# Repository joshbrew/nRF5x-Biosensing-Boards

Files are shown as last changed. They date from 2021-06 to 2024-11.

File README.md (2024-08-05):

# nRF52/53 Biosensing Boards

This contains our working prototypes for using nRF52 and nRF53 microcontrollers (ARM + BLE5) with low cost sensors. [Doc](https://docs.google.com/document/d/1gOrWiBDynYziCYDMF4r1Rw85PXo9JbuBrYJEEkW2U-c/edit?usp=sharing). 

License: AGPL v3.0 copyleft (public domain). You may do whatever you want with our designs, but you are obligated to share your modifications and advancements publicly. This is in hopes of facilitating a better community around useful wearable medical hardware designs.

The current prototypes here are working breakout boards. They are pin compatible with several different modules while it's easy to spin up new designs with similar products by Fanstel.

Features Zephyr RTOS test firmware, which is hardware-agnostic. 

### Designs included

- BT40/BT840, pin compatible with any Fanstel BT-series but mind the pinouts as not all will work without modification, but most should.
- BC840M
- BC40M
- BT832A (do not use, this was our first attempt)

### Firmware included

- nRF5340
- nRF52840
- nRF52810 (for the BT832A prototype)

### Sensor Support 
- ADS131M08 (8 channel sigma delta converter), there is one on-board 
- MPU6050 accelerometer
- QMC5883L magnetometer (for 9-axis movement when combined with MPU6050)
- MAX30102 pulse oximeter, 
- BMP/BME280 environmental sensor, 
- Additional 8 channel ADS131M08 for up to 16 raw data channels, each individually configurable. 
- MAX98357A Audio output amplifier
- B079Q8G7N1 PDM MEMS microphone

### [Driver Docs](https://docs.google.com/document/d/1eThhvpdm9zZMaKTB0dwuHXi1aBz_5ESBecHRZPxs0kE/edit?usp=sharing)

You can fairly easily add more sensor modules, which are all plug-and-play so the board can run with any combination of sensors. We'll clean this up more as we go for easier customization and feature inclusions. The BT840/BT40, BC840M, and BC40M prototypes include battery chargers with TVS diodes for safety so the boards could be FDA-approved.

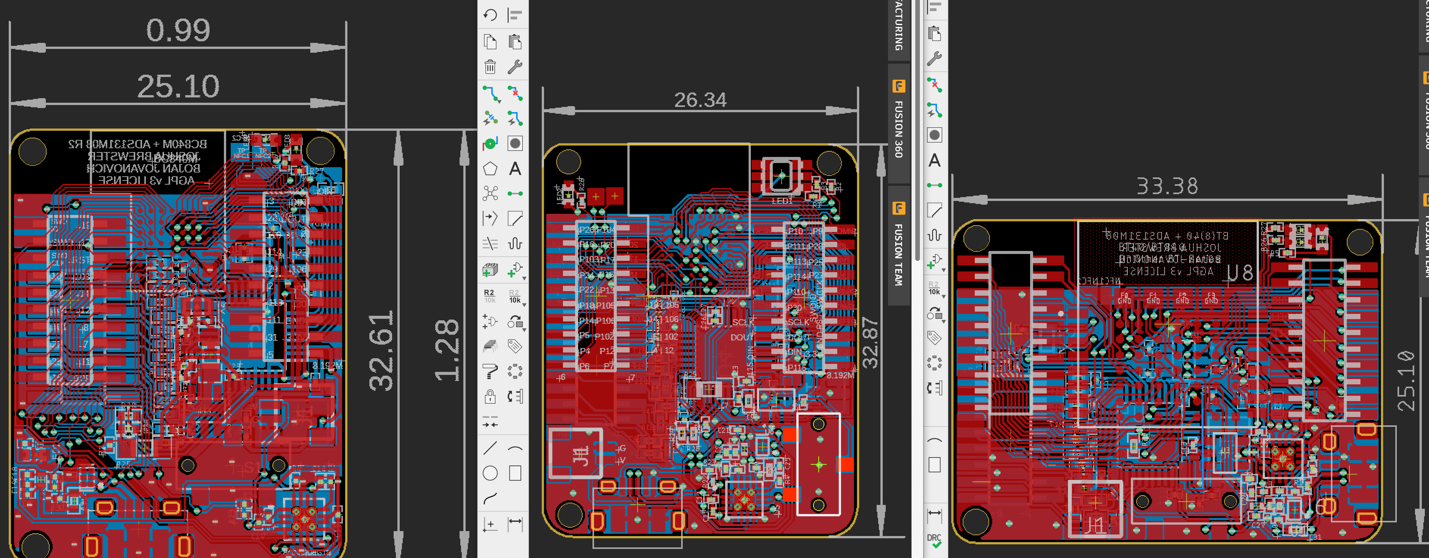
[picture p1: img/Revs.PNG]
breakout


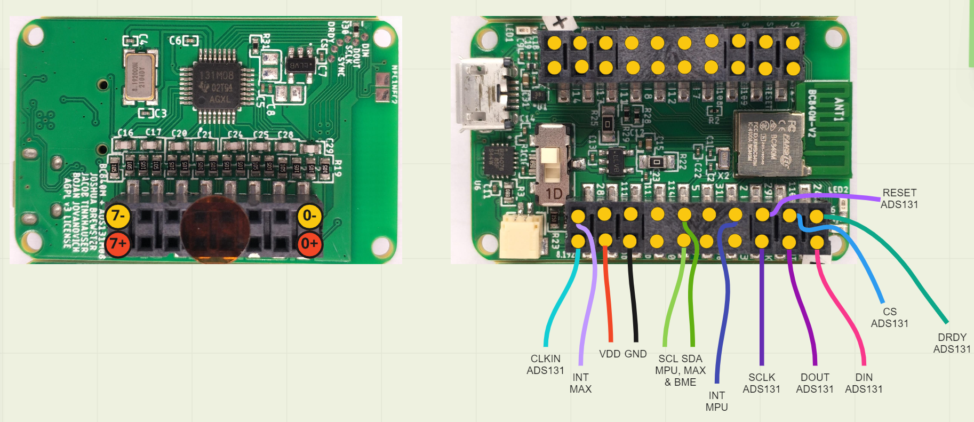
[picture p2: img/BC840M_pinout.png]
bc840m


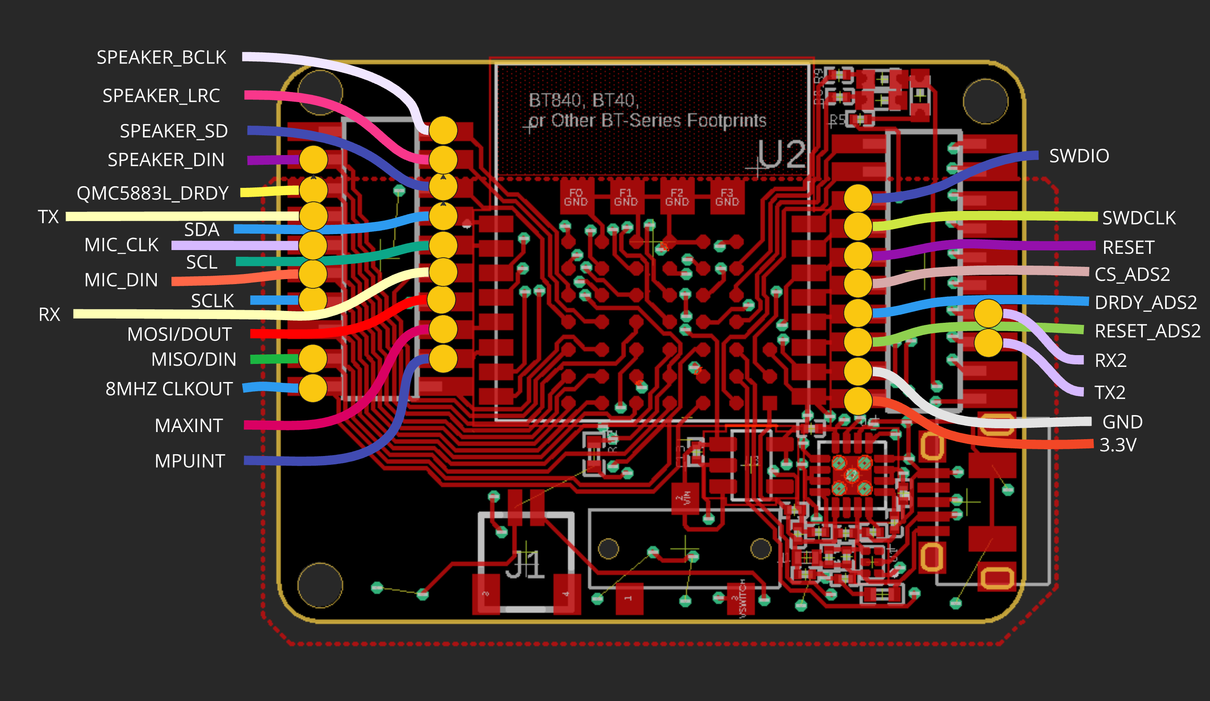
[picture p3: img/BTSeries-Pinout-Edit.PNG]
bt40


Version 3 (BT40/BT840, BC840M R2 & BC40M R1 designs) by Joshua Brewster and Bojan Jovanovich. Firmware by Bojan Jovanovich, drawings and frontend software by Josh Brewster. 

Versions 2 (BC840M R1) by Joshua Brewster, Jacob Tinkhauser, Bojan Jovanovich. Firmware by Bojan, drawings and frontend software by Josh Brewster. Testing and early design phase included Jacob Tinkhauser. 

Version 0 (BT832A) by Joshua Brewster, Jacob Tinkhauser, and Bojan Jovanovich. Firmware by Bojan and Jacob, drawings and frontend by Joshua Brewster.

Developed for creating open source wearables for biofeedback and treatment recovery monitoring.

Related:
- [BLE & USB Web drivers and debugger](https://github.com/joshbrew/device_debugger)

Below results with the ADS131M08 doing quick tests. Noise floor was around 350 nanovolts when shorted. These are not final results but show lots of promise.

- EEG alpha waves (spikes are blinks through a digital bandpass filter)
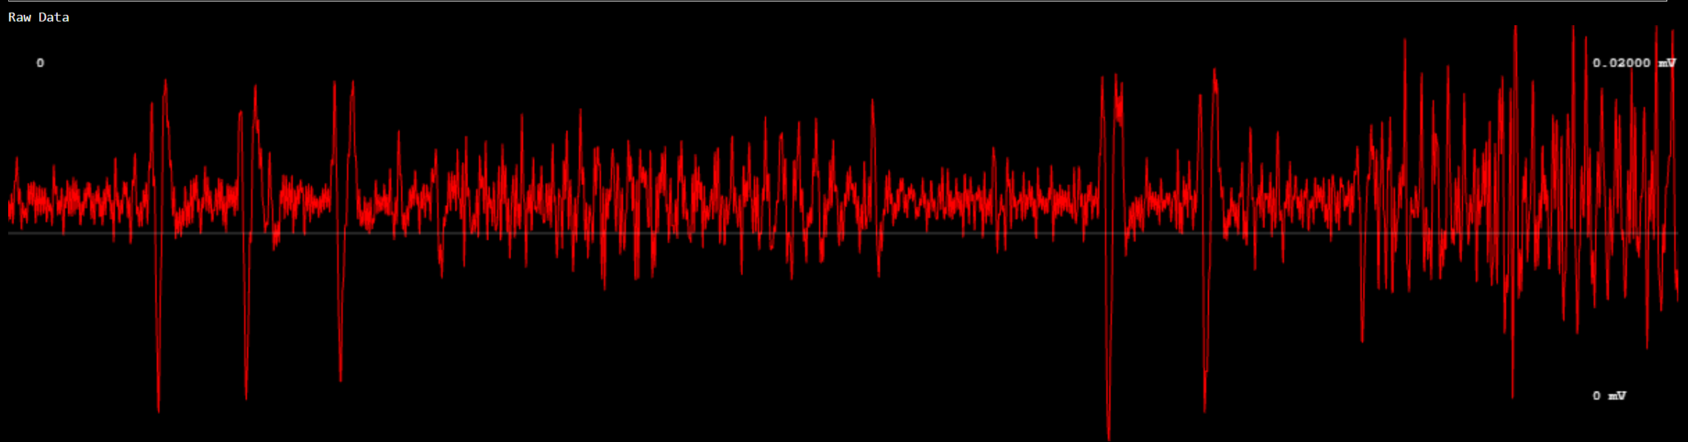
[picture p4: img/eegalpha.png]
EEG


- ECG with additional digital 50Hz lowpass
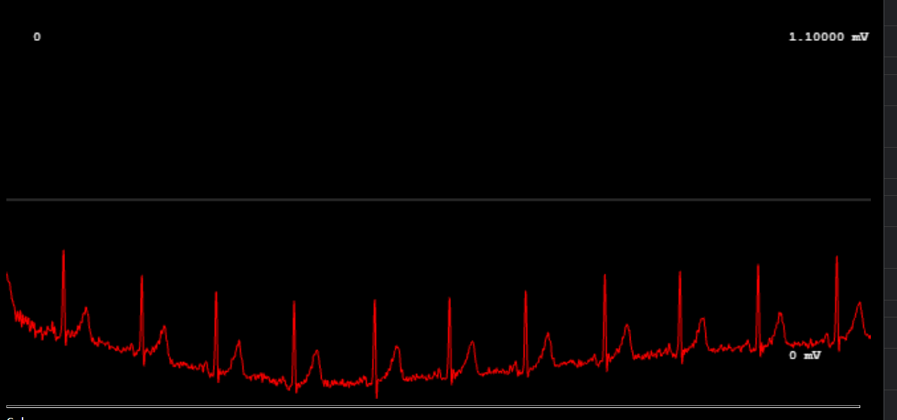
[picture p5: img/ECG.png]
ECG


- Raw EOG
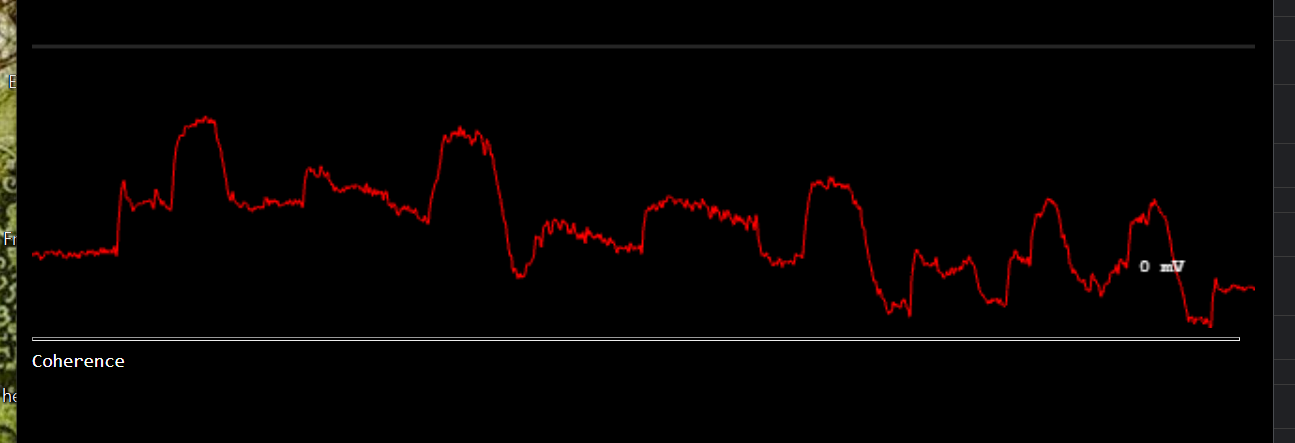
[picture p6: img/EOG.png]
EOG


- Raw PPG wave (red LED + Photodiode BPW 34 w/ basic 1MOhm + 200pf lowpass filter)
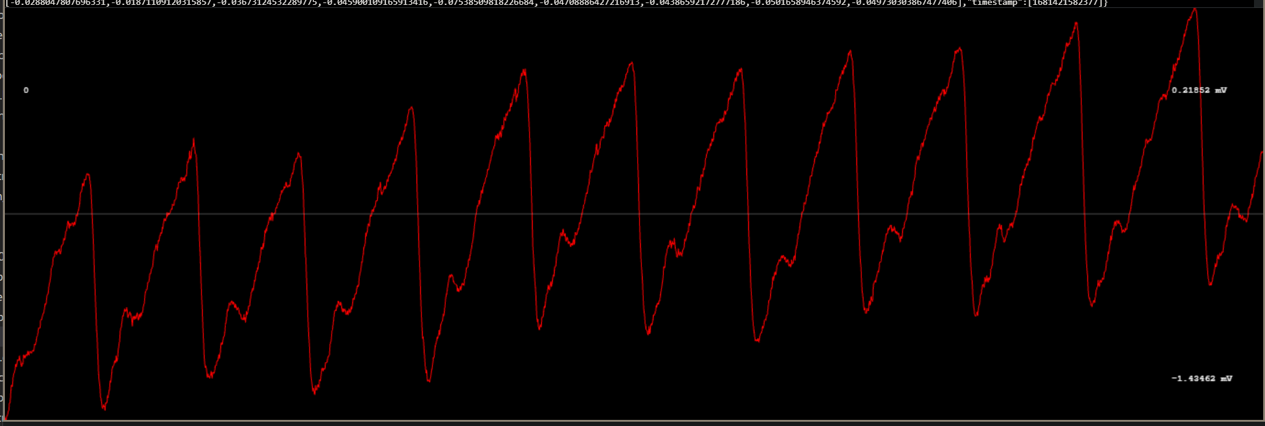
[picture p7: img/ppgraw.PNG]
PPG


Note the ADS131M08 is pretty much completely useless on USB power as we do not have digital or power isolators. We recommend sticking with the Bluetooth 5 and battery support except for when debugging.

Todos:
- PDFs, but the free EAGLE version works for these simple boards.
- Make the firmware more API-like for adding sensors and easier to cross-compile.
- Upgrade zephyr firmware version to latest Nordic SDK version, need to redo dependencies.
- Finish NFC integration
- Fine tune data throttling

Bug fixing notes:
- Bojan note (old, worked elsewhere): Sensors not booting, build error with the audio settings

Exploratory:
- SD card
- Integration with a graphical device (stay tuned :-))
- Vibration motor integration (just a GPIO on/off)
- Frontend controls for the whole command interface in javascript
- GPS (e.g. LG77L)
- More design modularity, e.g. attachments and hubs

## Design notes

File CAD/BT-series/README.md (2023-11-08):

Designed for BT840 but compatibile with all Fanstel BT-series microcontrollers (incl BT40 minus the single extra GPIO)

Low cost, minimal size, all 6 mil traces.

Refer to datasheet for BT40 pinout, the board is configured for the BT840 which also has one less pin:

https://www.mouser.com/datasheet/2/915/Fanstel_08262021_BT40F_Product_Specificationsv1_01-2530184.pdf

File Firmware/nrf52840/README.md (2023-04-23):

# nRF52840 Zephyr
Working repository for the nRF52 Zephyr firmware, made for a [BC840M prototype](https://github.com/moothyknight/nRF52-Biosensing-Boards)

Recommended build tools: nRFConnect with VSCode. 

Instructions:
- [Install](https://nrfconnect.github.io/vscode-nrf-connect/) nRFConnect for VSCode. We used SDK version 1.9.1 in the toolchain manager.
- Open this repo in VSCode
- In VSCode, in the nRFConnect extension under the APPLICATIONS tab, select the "Add Build Configuration" button to the right of the main folder name. Select the correct board, nrf52840dk_nrf52840, and click Build Configuration. Make sure prj.conf is selected as the configuration below it.
- Connect the nRF52-dk via usb with the flash pins wired to the custom PCB. Note: wire VTG to VDD on the DK, then VDDnRF to the custom PCB's VDD pin, then the rest of the SW/Reset/Gnd pins.
- In VSCode, in the nRFConnect extension under the ACTIONS tab, select "Flash" to build and flash the code

Include the extra Cmake argument:
- `-DDTC_OVERLAY_FILE:STRING="path/to/nrf52840dk_nrf52840.overlay"`

- You may edit pinouts in the main.cpp and overlay files.

You may need to manually install gnu-arm-embedded software. 

We used the nRF52 development board which is a J-LINK device for flashing. 

Was also able to use a 1 dollar STM32 blue pill to flash a built hex file manually. 

Device sensor test: http://modules.brainsatplay.com/

Debugger demo: https://devicedebugger.netlify.app/

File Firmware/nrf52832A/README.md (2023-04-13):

# BT832_Zephyr
Working repository for the nRF52 Zephyr firmware, made for a [BT832A prototype (24KB)](https://github.com/moothyknight/nRF52-Biosensing-Boards/tree/main/CAD/BT832_OLD)

Instructions:
- [Install](https://nrfconnect.github.io/vscode-nrf-connect/) nRFConnect for VSCode. We used SDK version 1.9.1 in the toolchain manager.
- Open this repo in VSCode
- In VSCode, in the nRFConnect extension under the APPLICATIONS tab, select the "Add Build Configuration" button to the right of the repo name, BT832_Zephyr. Select the correct board, nrf52dk_nrf52810, and click Build Configuration.
- Connect the nRF52DK via usb with the flash pins wired to the custom PCB. Note: wire VTG to VDD on the DK, then VDDnRF to the custom PCB's VDD pin, then the rest of the SW/Reset/Gnd pins.
- In VSCode, in the nRFConnect extension under the ACTIONS tab, select "Flash" to build and flash the code

Extra CMAKE Argument:
`-DDTC_OVERLAY_FILE:STRING="path/to/zephyr/nrf52dk_nrf52810.overlay"`

You may edit the pin configurations in the main.cpp and overlay files.

You may need to manually install gnu-arm-embedded software. 

We used the nRF52 development board which is a J-LINK device for flashing.

Device sensor test: http://modules.brainsatplay.com/

Debugger demo: https://devicedebugger.netlify.app/ 

The BT832A can only run the EMG chip due to the 24kb size limit, but it's dirt cheap.

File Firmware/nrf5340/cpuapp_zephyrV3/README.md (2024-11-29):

# nrf5340 Zephyr
Working repository for the nRF52 Zephyr firmware, made for a [BT40/BC40M prototype](https://github.com/moothyknight/nRF52-Biosensing-Boards)

Recommended build tools: nRFConnect with VSCode. 

For pinouts refer to datasheet: https://www.mouser.com/datasheet/2/915/Fanstel_08262021_BT40F_Product_Specificationsv1_01-2530184.pdf or see the BT-series CAD folder for pinout screenshots.

Note, the BT-series design is using the BT840 footprint, so correlate the pins via the datasheet.

Instructions:
- [Install](https://nrfconnect.github.io/vscode-nrf-connect/) nRFConnect for VSCode.  We used SDK version 2.8.0 in the toolchain manager. 
- Open this repo in VSCode and launch the nRFConnect menu within VSCode
- In VSCode, in the nRFConnect extension under the APPLICATIONS tab, select the "Add Build Configuration" button to the right of the main folder name (cpuapp). Select the correct board, nrf5340dk_nrf5340_cpuapp, and click Build Configuration. Make sure prj.conf is selected as the configuration below it.
- Connect the nRF52-dk via usb with the flash pins wired to the custom PCB. Note: wire VTG to VDD on the DK, then VDDnRF to the custom PCB's VDD pin, then the rest of the SW/Reset/Gnd pins.
- In VSCode, in the nRFConnect extension under the ACTIONS tab, select "Flash" to build and flash the code

Include the extra Cmake argument in the build configuration:
- `-DDTC_OVERLAY_FILE:STRING="path/to/nrf5340dk_nrf5340.overlay"`

For cpunet do the same thing, but without the overlay file.

- You may edit pinouts in the main.cpp and overlay files.

You may need to manually install gnu-arm-embedded software. 

We used the nRF53 (53! The nRF52DK did not work for us) development board which is a J-LINK device for flashing. 

Was also able to use a 1 dollar STM32 blue pill to flash a built hex file manually.

Device sensor test: http://modules.brainsatplay.com/

Debugger demo: https://devicedebugger.netlify.app/

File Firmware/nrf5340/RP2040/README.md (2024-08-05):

# RPI PICO C++ Project

[Windows SDK installation](https://www.raspberrypi.com/news/raspberry-pi-pico-windows-installer/)

You also need CMake and VSCommunity 2022 in the current config to access the C/C++/ASM compilers and NMake, and ensure the tool path is in your System or User ENV Path:

e.g. C:\Program Files\Microsoft Visual Studio\2022\Community\VC\Tools\MSVC\14.39.33519\bin\Hostx64\x64

Also set the env variables (or declare manually in CMakeLists.txt)

PICO_SDK_PATH=C:\Program Files\Raspberry Pi\Pico SDK v1.5.1\pico-sdk

PICO_TOOLCHAIN_PATH=C:\Program Files\Raspberry Pi\Pico SDK v1.5.1\gcc-arm-none-eabi

In Windows, if using the installer provided at the previous link:

[Pico SDK github](https://github.com/raspberrypi/pico-sdk)

[Raspberry Pi Pico SDK PDF (linux oriented)](https://datasheets.raspberrypi.com/pico/getting-started-with-pico.pdf)

# Build

In VSCode, open RP2040

`cd App` (if starting in this README directory)

`mkdir binaries` or `cd ./binaries`

`cmake -G "NMMake Makefiles" ..`

`nmake`

# UF2 Binary

In `./binaries/main` after making, you can drag and drop main.uf2 into your RP2040 plugged in via USB to program it.

This will remove the USB detection when it flashes successfully. 

To reset, on the RP2040, hold down the reset button, then hold down the boot button and press the reset button. It will show up again as a USB device.

# COMMANDS

The RP2040 expects commands to begin alternating LEDs, you can set up more with in the main.cpp

- `A\n` - 250Hz period for pins defined in main();
- `B\n` - 500Hz period
- `C\n` - 1000Hz period
- `D\n` - 2000Hz period

Stop PWM Command:

- `STOP\n`: Stops the PWM operation.
Enter Deep Sleep Command:

- `SLEEP\n`: Puts the system into deep sleep for a specified duration.
Wake Up and Resume PWM Command:

- `WAKE\n`: Wakes up the system and resumes PWM operation.
Set Custom Parameters:

Commands with a parameter followed by a value, separated by a space.
Examples:
- `PULSEWIDTH 300\n`: Sets pulseWidthUs to 300 microseconds.
- `PERIOD 4000\n`: Sets periodUs to 4000 microseconds.
- `INITIALDELAY 500\n`: Sets initialDelayUs to 500 microseconds.

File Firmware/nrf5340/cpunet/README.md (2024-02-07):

# nrf5340 Zephyr
Working repository for the nRF52 Zephyr firmware, made for a [BT40/BC40M prototype](https://github.com/moothyknight/nRF52-Biosensing-Boards)

Recommended build tools: nRFConnect with VSCode.

Instructions:
- [Install](https://nrfconnect.github.io/vscode-nrf-connect/) nRFConnect for VSCode.  We used SDK version 1.9.1 in the toolchain manager. Note v2023.11.301 of the main plugin would not work for us and others. Use v2023.11.24
- Open this repo in VSCode and launch the nRFConnect menu within VSCode
- In VSCode, in the nRFConnect extension under the APPLICATIONS tab, select the "Add Build Configuration" button to the right of the main folder name (cpunet). Select the correct board, nrf5340dk_nrf5340_cpunet, and click Build Configuration. Make sure prj.conf is selected as the configuration below it.
- Connect the nRF52-dk via usb with the flash pins wired to the custom PCB. Note: wire VTG to VDD on the DK, then VDDnRF to the custom PCB's VDD pin, then the rest of the SW/Reset/Gnd pins.
- In VSCode, in the nRFConnect extension under the ACTIONS tab, select "Flash" to build and flash the code

You do not need to include the overlay file in `cpunet`, only in `cpuapp`. Each must be compiled and flashed independently.

- You may edit pinouts in the main.cpp and overlay files.

You may need to manually install gnu-arm-embedded software. 

We used the nRF53 (53! The nRF52DK did not work for us) development board which is a J-LINK device for flashing. 

Was also able to use a 1 dollar STM32 blue pill to flash a built hex file manually.

Device sensor test: http://modules.brainsatplay.com/

Debugger demo: https://devicedebugger.netlify.app/

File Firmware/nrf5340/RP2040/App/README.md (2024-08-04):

# RPI PICO C++ Project

[Windows SDK installation](https://www.raspberrypi.com/news/raspberry-pi-pico-windows-installer/)

You need to set two environment variables afterward.

PICO_SDK_PATH

PICO_TOOLCHAIN_PATH

In Windows, if using the installer provided at the previous link:

PICO_SDK_PATH=C:\Program Files\Raspberry Pi\Pico SDK v1.5.1\pico-sdk

PICO_TOOLCHAIN_PATH=C:\Program Files\Raspberry Pi\Pico SDK v1.5.1\gcc-arm-none-eabi

[Pico SDK github](https://github.com/raspberrypi/pico-sdk)

[Raspberry Pi Pico SDK PDF (linux oriented)](https://datasheets.raspberrypi.com/pico/getting-started-with-pico.pdf)

# Build

`cmake CMakeLists.txt`

# UF2 Binary

In `./binaries` after bundling, you can drag and drop main.uf2 into your RP2040 plugged in via USB to program it.

# COMMANDS

The RP2040 expects commands to begin alternating LEDs, you can set up more with in the main.cpp

- `A\n` - 250Hz period for pins defined in main();
- `B\n` - 500Hz period
- `C\n` - 1000Hz period
- `D\n` - 2000Hz period

Stop PWM Command:

- `STOP\n`: Stops the PWM operation.
Enter Deep Sleep Command:

- `SLEEP\n`: Puts the system into deep sleep for a specified duration.
Wake Up and Resume PWM Command:

- `WAKE\n`: Wakes up the system and resumes PWM operation.
Set Custom Parameters:

Commands with a parameter followed by a value, separated by a space.
Examples:
- `PULSEWIDTH 300\n`: Sets pulseWidthUs to 300 microseconds.
- `PERIOD 4000\n`: Sets periodUs to 4000 microseconds.
- `INITIALDELAY 500\n`: Sets initialDelayUs to 500 microseconds.

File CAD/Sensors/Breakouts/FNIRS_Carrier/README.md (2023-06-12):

- Use the BT-series boards. The pinouts are defined for the BT840 specifically.

- ADS131M08 breakout for 8+ more channels at https://github.com/joshbrew/ADS131M08_Arduino
- FNIRS carrier board for DIY_DOT project.
- See the DOT Headset boards at at https://github.com/joshbrew/DIY_DOT

- MAX30102 breakout and the unfinished biosensing shield breakout by Arthur Jordan

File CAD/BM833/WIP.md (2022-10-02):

Just need to wire the GPIO, use the pin-compatible I/O for everything, not the extras that the BM833 has, so we can still use the BM840, BM832, etc.

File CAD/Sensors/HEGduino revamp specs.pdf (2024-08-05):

Ultra Low Cost FNIRS headband design, based on HEGduino (free source) by Josh Brewster

Overview:

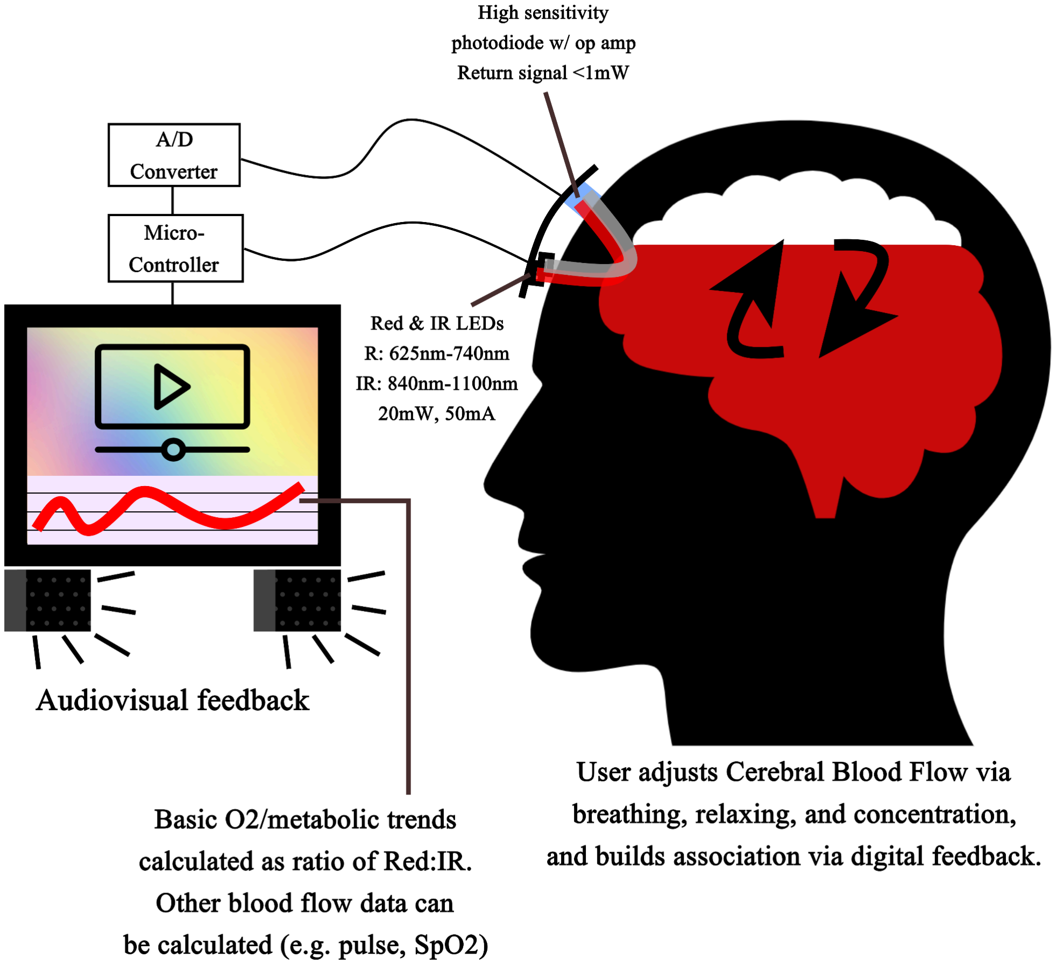
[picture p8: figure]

This project involves developing a low-cost Functional Near-Infrared Spectroscopy (FNIRS) headband, based on the free-source HEGduino platform. The hardware is essentially a pulse oximeter designed with specific sensor spacing to resolve deeper tissue signals. This technology, known as Hemoencephalography (HEG) in biofeedback applications, monitors blood flow and provides functional imaging for brain blood flow studies. We aim to create an affordable device for stress and breathing training, functioning similarly to an HRV monitor but worn on the head. I’ve included two possible specifications, we should quote for both as the first should be a little more straightforward but the second one is more scientifically valid and medically relevant.

Design 1 Hardware Specifications (lower fidelity than Design 2):

- Microcontroller:
- ESP32 WROOM32: Alternatively, the smaller ESP32-S (Bluetooth only) can be used. Downclock to 80MHz to extend battery life.
- nRF52810 or nRF52832: E.g., Fanstel BT832A or BT832, which offer better power efficiency. Both can be bootstrapped quickly with platform.io or Arduino and ready-made sensor libraries.
- Pulse Oximeter Sensor:
- MAX86141: Dual-channel sensor, capable of driving up to 6 LEDs.
- Photodiodes: BPW-34S, these are the best available and low cost.
- LEDs:
■ Domed 660nm or 740-770nm Red/Far Red LED: Domed LEDs preferred for a narrower cone of light created. Power level:
20mAh-50mAh (e.g., XZM2MR55W-3 by SunLED). Far red is better, just the pickings are slimmer.
■ Domed 840-880nm Infrared LED: Same power output level (e.g., XZTHI55W-3 by SunLED).
- Power and Connectivity:
- USB type C: For battery charging and debugging. Include TVS diodes on the battery charge portion for safety compliance.
- Lipo battery, safe, cheap, any size.

Firmware Requirements:

- Sensor Data Acquisition:
- MAX86141: Simultaneously senses photodiodes, filtering, and processing the signals internally.
- LED Driving: LEDs should operate at the highest rate possible, aiming for 50Hz-100Hz updates for optimal accuracy. Josh can advise on firmware settings.
- Data Transmission:
- Bluetooth: The microcontroller should transmit buffered sensor data byte packets. Data should be packed efficiently (e.g., 24-bit structure for 19-bit MAX86141 values).
- Commands and Debugging:
- Bluetooth Commands: Simple commands to power the device on/off and an inactivity timer for automatic shutdown.
- USB Debug Output: Output the same sensor packet data to USB as Bluetooth for consistency in parsing on the client side.

Visual Diagram
Idea is a flex PCB that covers the forehead with a row of sensors and LEDs:

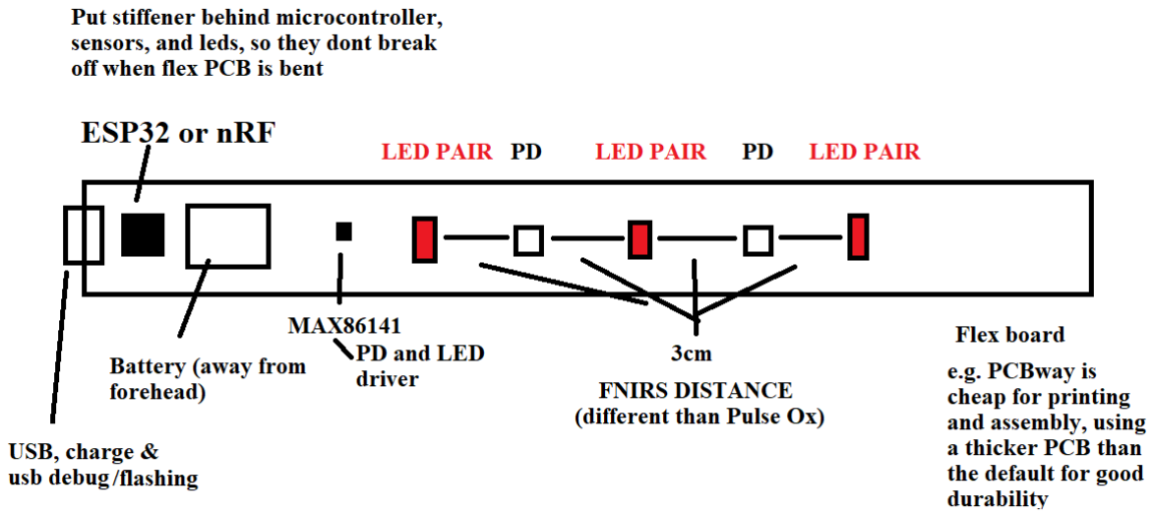
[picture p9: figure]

The diagram illustrates a flexible PCB covering the forehead with a row of sensors and LEDs. The design ensures that LED light does not leak to the photodiodes, requiring contact with the skin for accurate readings. Neoprene or similar materials may be used for comfort and to ensure a good seal.

For designing a case, the LEDs cannot leak light to the Photodiodes, all light must be pass via contact with the skin (forehead). The Mendi protrudes the LED and Photodiode contacts out, alternatively something soft that can conform to skin would be better and more comfortable, we just used neoprene before but we need a good seal on the sensors.

Output Expectations:

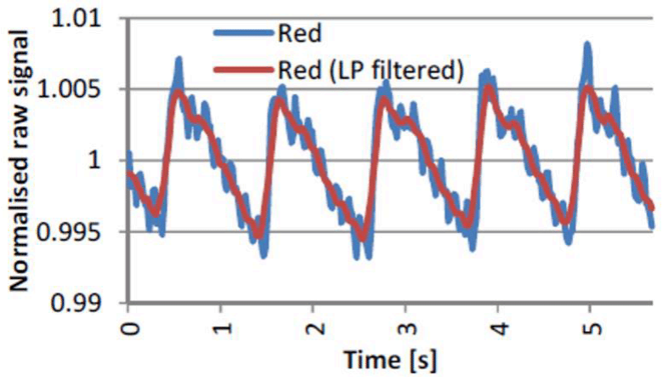
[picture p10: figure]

The expected data resembles typical pulse oximetry readings but with signals indicative of blood flow changes in deeper tissues. We’ll have one of these lines for each LED, red and infrared are compared to infer blood oxygen changes, and with multiple LED pairs we can compare across multiple sites.

Old Resources: https://github.com/joshbrew/HEG_ESP32_Delobotomizer

FNIRS sensor BOM:
https://docs.google.com/spreadsheets/d/1MgO6r2GJB0lHYTsHTYTxhSiRR5hWRgtUIwzvLXl5KvM/edit?usp=drive_link (https://docs.google.com/spreadsheets/d/1MgO6r2GJB0lHYTsHTYTxhSiRR5hWRgtUIwzvLXl5KvM/edit?usp=drive_link)

MAX86141 BOM:
https://docs.google.com/spreadsheets/d/1BV-0n5jjRR3LmGyLHRKKsdT_74nFn3pC/edit?usp=drive_link&ouid=115019542711496588778&rtpof=true&sd=true (https://docs.google.com/spreadsheets/d/1BV-0n5jjRR3LmGyLHRKKsdT_74nFn3pC/edit?usp=drive_link&ouid=115019542711496588778&rtpof=true&sd=true)

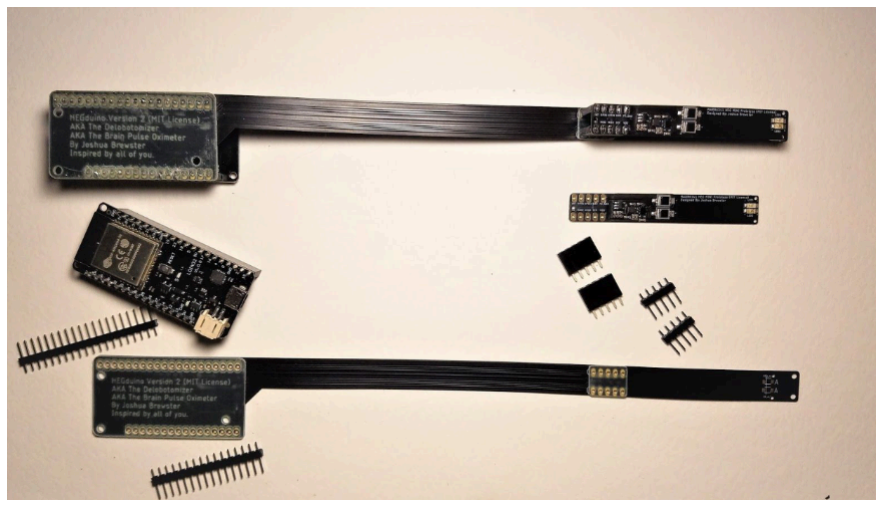
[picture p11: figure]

This configuration put both PDs together but we are looking for a different layout this time that gives us the fuller breadth of the forehead.

Design 2, superior hardware specs, state-of-the-art for this price point:

Hardware:

- Microcontroller:
- nRF52 or 53: For BLE5.
- RP2040: (e.g. Waveshare RP2040Zero for $4) Independent LED driver with up to 16 PWMs, requiring synchronization of ADS131 readings with LED pulses. RP2040 Zero may need a Darlington Transistor to increase current yield but we don’t need more than 20mAh, the RP2040 should be able to do up to 50mAh.
- Sensor ADC:
- ADS131M08 or M04: 4-8 channels 24-bit sigma delta, simultaneous sampling ADC.
- Photodiodes: BPW-34S, these are the best available and low cost.
- LEDs:

■ Domed 660nm or 740-770nm Red/Far Red LED: Domed LEDs preferred for a narrower cone of light created. Power level:
20mAh-50mAh (e.g., XZM2MR55W-3 by SunLED). Far red is better, just the pickings are slimmer.
■ Domed 840-880nm Infrared LED: Same power output level (e.g., XZTHI55W-3 by SunLED).
- Power and Connectivity:
- USB type C: For battery charging and debugging. Include TVS diodes on the battery charge portion for safety compliance.
- Lipo battery, safe, cheap, any size

Firmware Notes:

- Special care is required to synchronize PWM signals with ADS131M08 for precise LED pulse capturing.
- The overall functionality remains similar to the simpler design but with enhanced signal resolution.

More sophisticated design, same relative cost as the MAX86141 but much bigger punch:

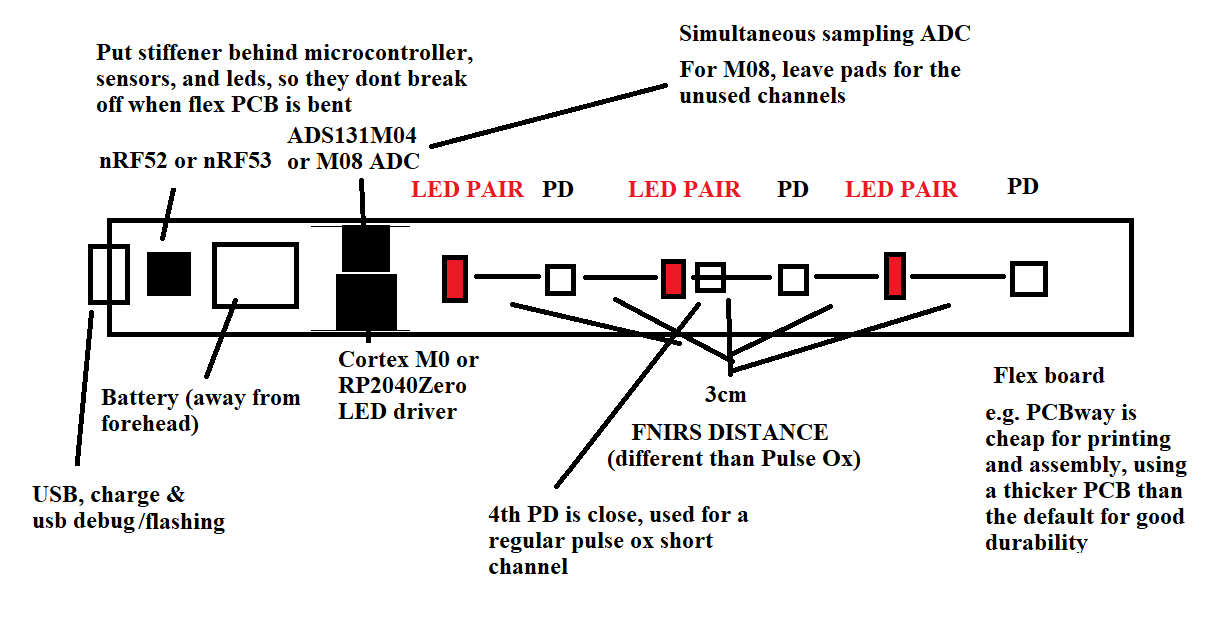
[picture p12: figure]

Note the short channel here is something seen on more advanced FNIRS designs for noise cancellation. It’s the best configuration we could come up with for 4 channels as it may get too wide otherwise. Based on the pairings this gives 5 FNIRS sites and maybe more if it’s sensitive enough to pick up the farther distances. We are working on testing this but the design is sound.Also for the non sensing components, keep those backside to not obstruct the forehead or bluetooth chip, power, etc.

Sample Designs and Additional Resources:

Our sample designs include development boards for RP2040/Cortex M0 and an nRF + ADS131M08 setup. The signal quality achieved is state-of-the-art.

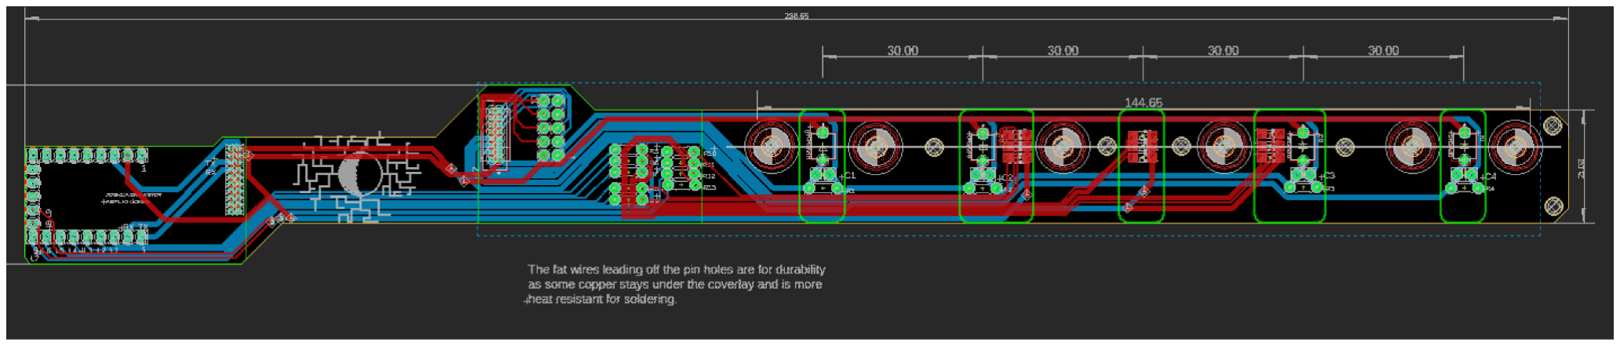
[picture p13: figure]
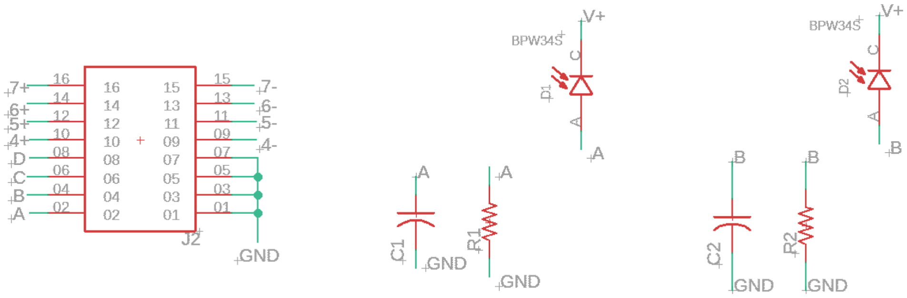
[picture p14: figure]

The photodiodes are configured in a simple low pass configuration, with negative ADC inputs to ground in this sigma-delta configuration. 100kOhm R and 100pF C works, can be adjusted.

A transimpedance amplifier is necessary for current to voltage conversion, not shown here. OPA381 is good. The PD readings otherwise will not be accurate. The readings also will settle out even when disabling the DC block filter on the ADC, but as long as it’s changing it sustains the power levels being read. For relative readings it’s fine but for pulse oximetry we probably need the amplifier.

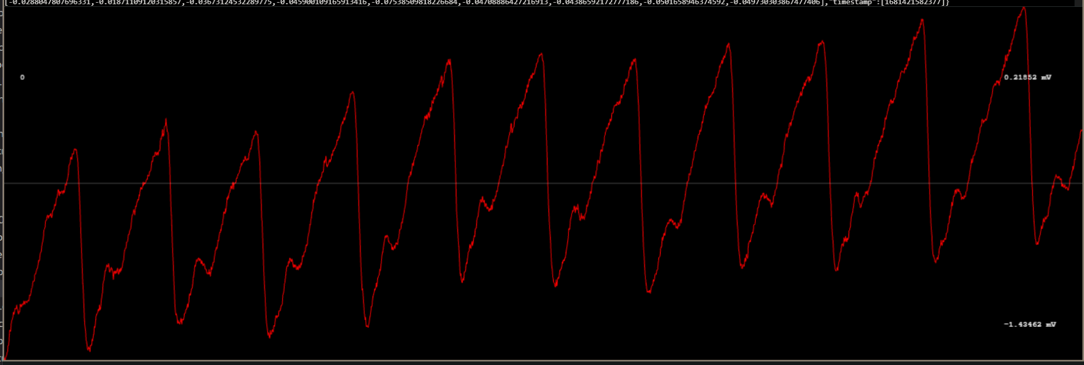
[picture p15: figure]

This is raw PPG data we got off this specification through our finger. This is ultra high quality data.

nRF Resources with an FDA-approvable PCB design: https://github.com/joshbrew/nRF5x-Biosensing-Boards

FNIRS sensor BOM:
https://docs.google.com/spreadsheets/d/1MgO6r2GJB0lHYTsHTYTxhSiRR5hWRgtUIwzvLXl5KvM/edit?usp=drive_link (https://docs.google.com/spreadsheets/d/1MgO6r2GJB0lHYTsHTYTxhSiRR5hWRgtUIwzvLXl5KvM/edit?usp=drive_link)

BOM samples:
E.g BT840
https://docs.google.com/spreadsheets/d/1_HJGfFERPbjsfyVsvAEBeEDxsZvMkjib/edit?usp=sharing&ouid=115019542711496588778&rtpof=true&sd=true (https://docs.google.com/spreadsheets/d/1_HJGfFERPbjsfyVsvAEBeEDxsZvMkjib/edit?usp=sharing&ouid=115019542711496588778&rtpof=true&sd=true)

E.g. BT40
https://docs.google.com/spreadsheets/d/1iG1TCaeJnqPSEQdyyh46KBVxkoCE-ekg/edit?usp=sharing&ouid=115019542711496588778&rtpof=true&sd=true (https://docs.google.com/spreadsheets/d/1iG1TCaeJnqPSEQdyyh46KBVxkoCE-ekg/edit?usp=sharing&ouid=115019542711496588778&rtpof=true&sd=true)

Another BT40 BOM (high overages though, not that necessary) https://docs.google.com/spreadsheets/d/1nfP5cUY5rJFIu8GrZoNSI9P1zyI8ZTMB/edit?usp=sharing&ouid=115019542711496588778&rtpof=true&sd=true (https://docs.google.com/spreadsheets/d/1nfP5cUY5rJFIu8GrZoNSI9P1zyI8ZTMB/edit?usp=sharing&ouid=115019542711496588778&rtpof=true&sd=true)
E.g BT832 cheap nRF52 option (note BT832A is the nRF52810, very small memory) https://docs.google.com/spreadsheets/d/1lq_YZKACqgZNz5KGheo3KygyKR9DUOsgQVpr5Snjju0/edit?usp=sharing (https://docs.google.com/spreadsheets/d/1lq_YZKACqgZNz5KGheo3KygyKR9DUOsgQVpr5Snjju0/edit?usp=sharing)

https://docs.google.com/spreadsheets/d/1RUlmk_B_wu3TRTACJXpPSCaapPaiVIjje_XyH6pws34/edit?usp=drive_link (https://docs.google.com/spreadsheets/d/1RUlmk_B_wu3TRTACJXpPSCaapPaiVIjje_XyH6pws34/edit?usp=drive_link) Peripheral stuff (not all directly relevant, just dev board sourcing, potential cheap route for sensor prefabs)

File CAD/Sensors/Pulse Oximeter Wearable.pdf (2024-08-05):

7Pulse Ox Wearable, open/free source designs by Josh Brewster

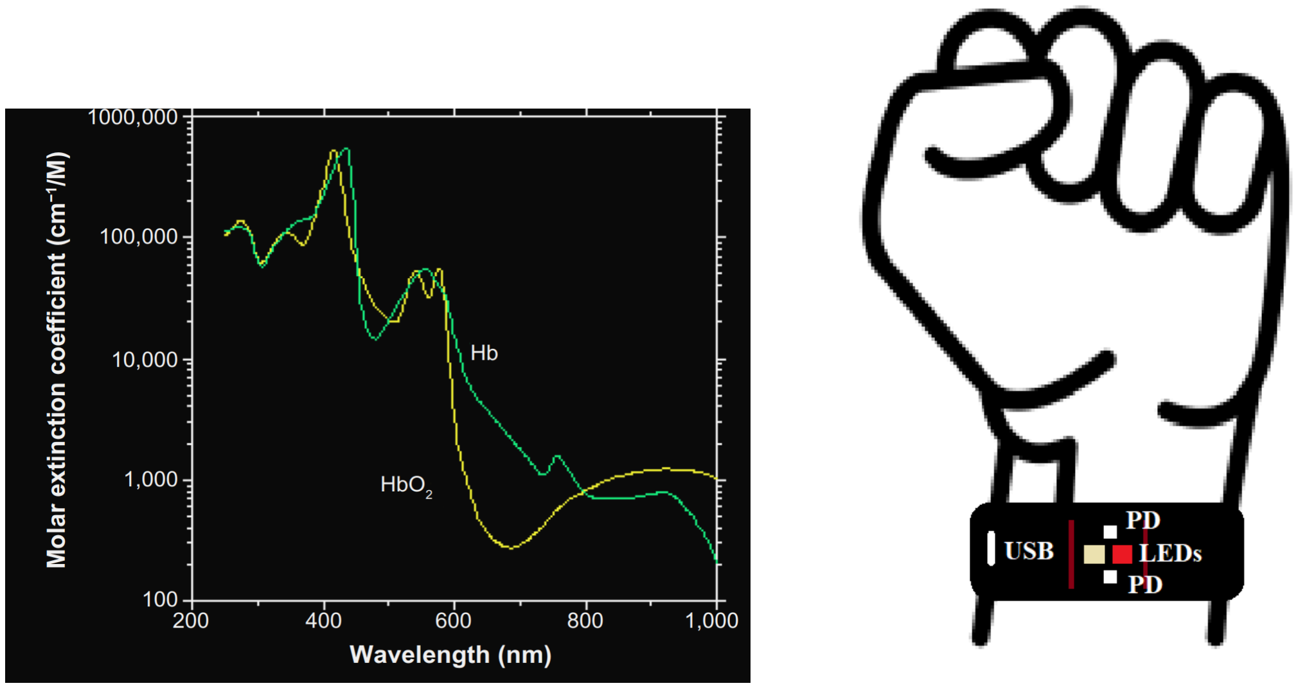
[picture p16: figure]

Band Design

The wearable band is a simple, thin pulse oximeter and motion-sensing band, designed to be rechargeable and to sample from the bottom of the wrist for optimal signal. Two designs are outlined: custom and canned. The custom design provides state-of-the-art results.

Design 1: Custom, More Reliable Pulse Ox, Cheapest Possible

This design aims to provide a more reliable pulse oximeter using custom components.

Hardware Specs

- Microcontroller: nRF52/53 BLE 5 controller
- ADC: ADS131M02 2-channel 24-bit simultaneous sampling sigma-delta ADC
- Photodiodes: 2 BPW34S high sensitivity photodiodes with a simple low pass filter circuit
- LEDs:
- 1 660nm Red LED (e.g., XZM2MR55W-3 by SunLED) Domed LEDs are better (narrower light cone)
- 1 840-880nm IR LED (e.g., XZTHI55W-3 by SunLED)
- Accelerometer: MPU6050 3-axis accelerometer (or a more current alternative)
- Magnetometer: QMC5883L 3-axis magnetometer (ideal for fall detection)
- Battery: Rechargeable LiPo battery port, small battery to fit in the case
- Charging: USB Type-C with TVS diodes for safety compliance
- Buttons: Small On/Off push button, plus 2 additional programmable buttons (e.g., for support or alert)
- Sampling: Bottom of the wrist (like over the artery/vein)
- Optional: Audio speaker for alarms (needs amplifier chip, e.g., MAX98357A)

Firmware Specs

- Operating System: Zephyr or Arduino (Zephyr is more advanced, but both are suitable for basic hardware)
- Communication: Bluetooth 4 or 5 (nRF52 has BLE5)
- Power Profile: Low power consumption (nRF is better for this)
- Sample Rate: The minimum is 250Hz on the ADS131, we can use a moving average firmware-side or BLE can handle the data in real time, we’ve tested plenty. Otherwise averaging to 125Hz, 75Hz, or 50Hz would be fine.
- Data Streaming: Stream raw LED data; use canned heart rate and SpO2 algorithms for pre-made PPGs with selected LEDs and PDs
- Filters: Preferably avoid hardware filters (e.g., for DC); more can be done with raw data without them

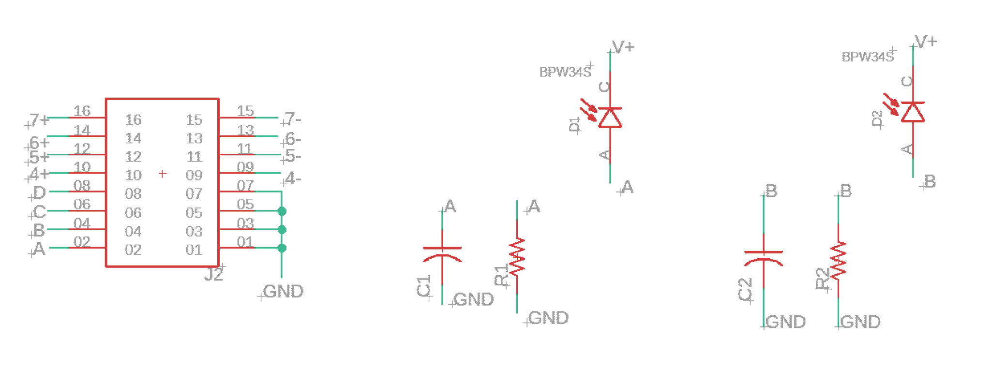
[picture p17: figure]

This is an ADS131M08 configuration, with 2 of 4 photodiodes shown, we use a simple RC filter and ground the negative input on the sigma delta ADC. 100kOhm R and 100pF C works, can be adjusted.

A transimpedance amplifier is necessary for current to voltage conversion, not shown here. OPA381 is good. The PD readings otherwise will not be accurate. The readings also will settle out even when disabling the DC block filter on the ADC, but as long as it’s changing it sustains the power levels being read. For relative readings it’s fine but for pulse oximetry we probably need the amplifier.

Hardware resources, includes nRF and peripheral quotes: https://github.com/joshbrew/nRF5x-Biosensing-Boards

BOM samples:
E.g BT840
https://docs.google.com/spreadsheets/d/1_HJGfFERPbjsfyVsvAEBeEDxsZvMkjib/edit?usp=sharing&ouid=115019542711496588778&rtpof=true&sd=true (https://docs.google.com/spreadsheets/d/1_HJGfFERPbjsfyVsvAEBeEDxsZvMkjib/edit?usp=sharing&ouid=115019542711496588778&rtpof=true&sd=true)

E.g. BT40
https://docs.google.com/spreadsheets/d/1iG1TCaeJnqPSEQdyyh46KBVxkoCE-ekg/edit?usp=sharing&ouid=115019542711496588778&rtpof=true&sd=true (https://docs.google.com/spreadsheets/d/1iG1TCaeJnqPSEQdyyh46KBVxkoCE-ekg/edit?usp=sharing&ouid=115019542711496588778&rtpof=true&sd=true)

Another BT40 BOM (high overages though, not that necessary) https://docs.google.com/spreadsheets/d/1nfP5cUY5rJFIu8GrZoNSI9P1zyI8ZTMB/edit?usp=sharing&ouid=115019542711496588778&rtpof=true&sd=true (https://docs.google.com/spreadsheets/d/1nfP5cUY5rJFIu8GrZoNSI9P1zyI8ZTMB/edit?usp=sharing&ouid=115019542711496588778&rtpof=true&sd=true)
E.g BT832 cheap nRF52 option (note BT832A is the nRF52810, very small memory) https://docs.google.com/spreadsheets/d/1lq_YZKACqgZNz5KGheo3KygyKR9DUOsgQVpr5Snjju0/edit?usp=sharing (https://docs.google.com/spreadsheets/d/1lq_YZKACqgZNz5KGheo3KygyKR9DUOsgQVpr5Snjju0/edit?usp=sharing)

https://docs.google.com/spreadsheets/d/1RUlmk_B_wu3TRTACJXpPSCaapPaiVIjje_XyH6pws34/edit?usp=drive_link (https://docs.google.com/spreadsheets/d/1RUlmk_B_wu3TRTACJXpPSCaapPaiVIjje_XyH6pws34/edit?usp=drive_link) Peripheral stuff (not all directly relevant, just dev board sourcing, potential cheap route for sensor prefabs)

This firmware will work out of the box for either design if we use nRF52 or 53, the boards just need a redesign for a tighter integration of chipsets.

Output Expectations:

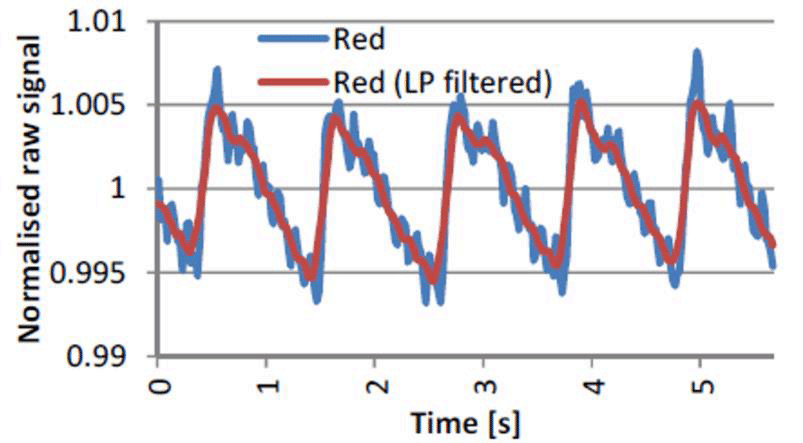
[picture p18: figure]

Pulse oximeter data is a wave like this. We compare two wavelengths as means to assess blood oxygen content, and more.

Our custom setup result will look like this using the exact specs in design 1:


This is unfiltered at 250Hz, the minimum sampling rate on the ADS131 without using global chop, but note this is state of the art quality PPG data, This is not a normal level of detail and signal cleanliness and we did not have to use any special configuration on the ADC.

More sampling data gives us more to diagnose and filter. Design 2 would be unprecedented quality for a low cost design and reflects our more up to date work. Realistically it should cost the same as the first design for physical hardware.

Design 2: Cheapest Possible, Bottom of the Barrel BLE Streaming Pulse Ox

This design focuses on cost-efficiency with pre-made pulse oximeter units.

Hardware Specs

- Microcontroller: ESP32 or nRF52/53 Bluetooth (Fanstel chips are cheap nRF options)
- Pulse Ox Unit: MAX30102/5 or other pre-made pulse ox units that are cheap in bulk
- Accelerometer: MPU6050 3-axis accelerometer (or a more current alternative)
- Magnetometer: QMC5883L 3-axis magnetometer (ideal for fall detection and motion artifact removal)
- Battery: Rechargeable LiPo battery port, small battery to fit in the case
- Charging: USB Type-C with TVS diodes for safety compliance
- Buttons: Small On/Off push button, plus 2 additional programmable buttons (e.g., for support or alert)
- Sampling: Bottom of the wrist (like over the artery/vein)
- Optional: Audio speaker for alarms

Firmware Specs (largely the same as design 1, just different sensor AFE)

- Operating System: Zephyr or Arduino (Zephyr is more advanced, but both are suitable for basic hardware)
- Communication: Bluetooth 4 or 5 (nRF52 has BLE5)
- Power Profile: Low power consumption (nRF is better for this)
- Sample Rate: 50Hz-100Hz (50Hz is acceptable, 100Hz is better; nRF can pack samples into ~30 sample packets)
- Data Streaming: Stream raw LED data; use canned heart rate and SpO2 algorithms for pre-made PPGs with selected LEDs and PDs
- Filters: Preferably avoid hardware filters (e.g., for DC); more can be done with raw data without them

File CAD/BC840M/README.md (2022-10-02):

We tested the BC840M successfully and made a bunch more versions now that we can be confident in it. We will continue testing these designs so expect more iterations.

Note the previous version had 1MOhm resistors on the signal inputs, this was found to generate too much noise while removing those granted us crystal clear ECG and EEG data, measuring wrist ECG and FP1 alpha waves. Photodiodes work on the default ADS131M08 configuration we provided as well, and we got PPG signal using the BPW34S photodiodes and a transimpedance amplifier.

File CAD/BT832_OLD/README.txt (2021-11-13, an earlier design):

BT832A (nrf52810) Test results:

BLE AND UART FIRMWARE TEST - SUCCESS
500SPS ADS131M08 BLE TEST - SUCCESS

USB POWER TEST - FAIL, NO VOLTAGE DIVIDER
BATTERY POWER TEST - FAIL, CHOSE A DUMB BATTERY CIRCUIT TO COPY

DON'T USE THESE DESIGNS WITHOUT FIXING OR REMOVING THE POWER CHARGING/USB INTERFACE.

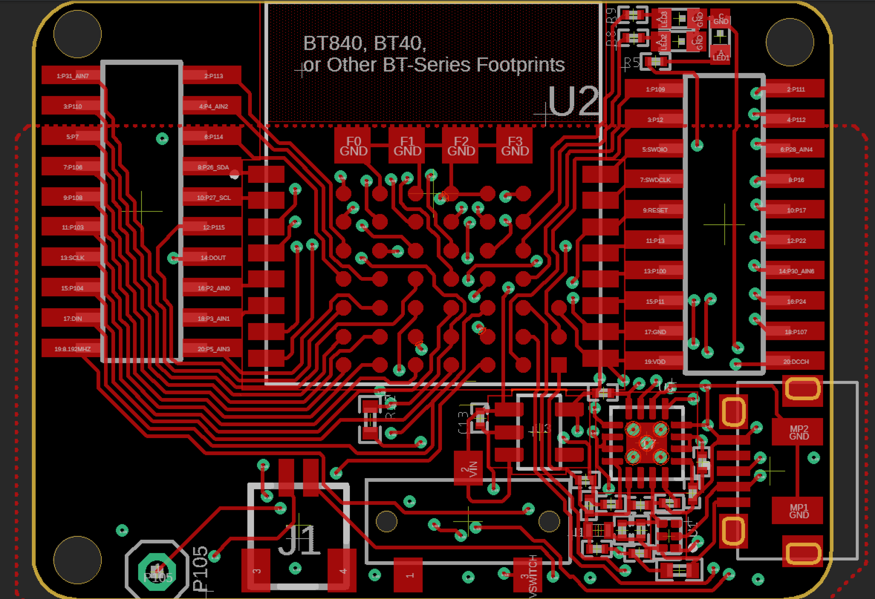
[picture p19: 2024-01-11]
CAD/BT-series/BT840PINOUT.PNG

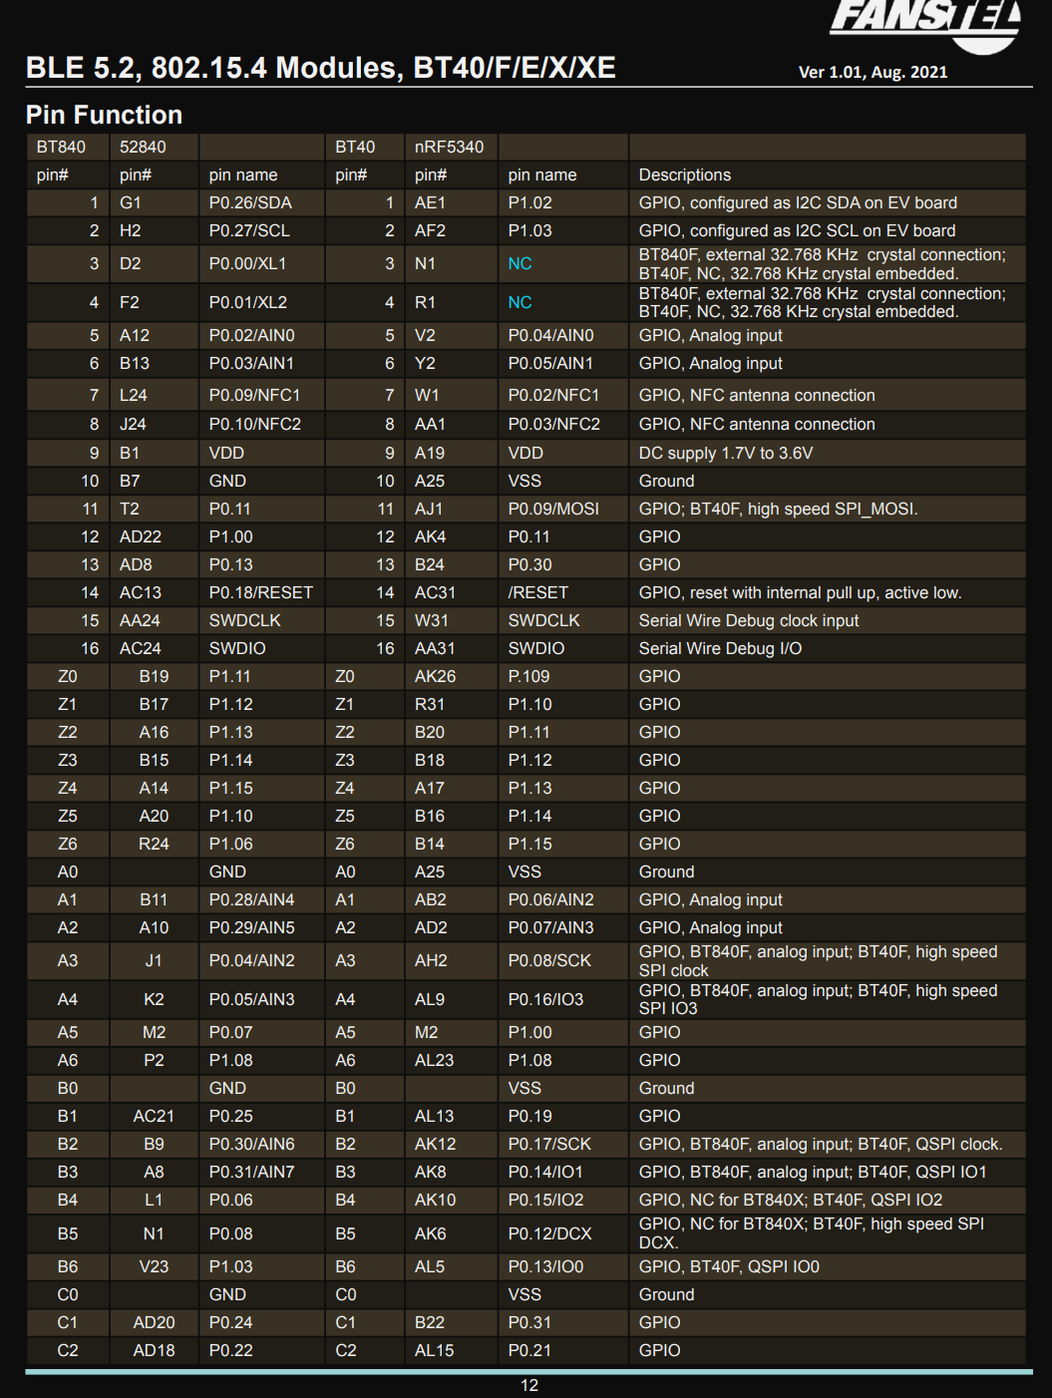
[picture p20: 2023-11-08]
CAD/BT-series/pinout1.PNG

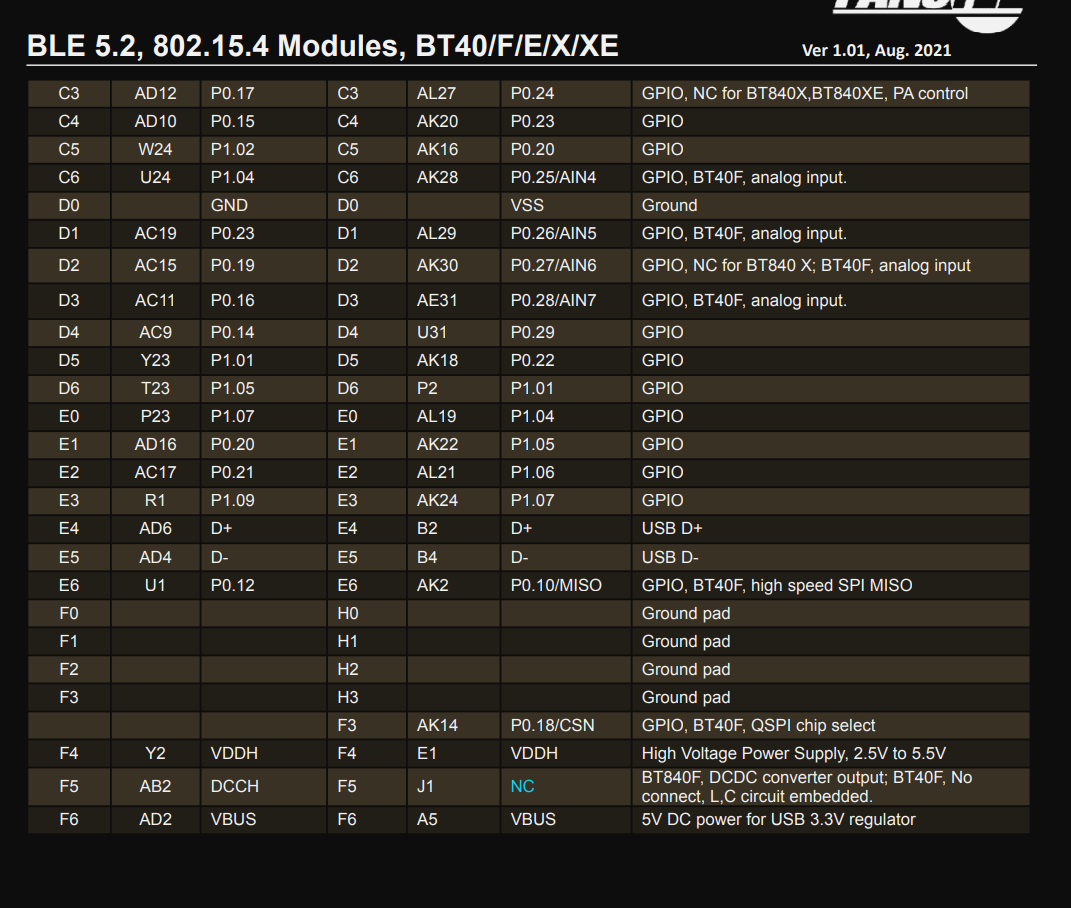
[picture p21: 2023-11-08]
CAD/BT-series/pinout2.PNG

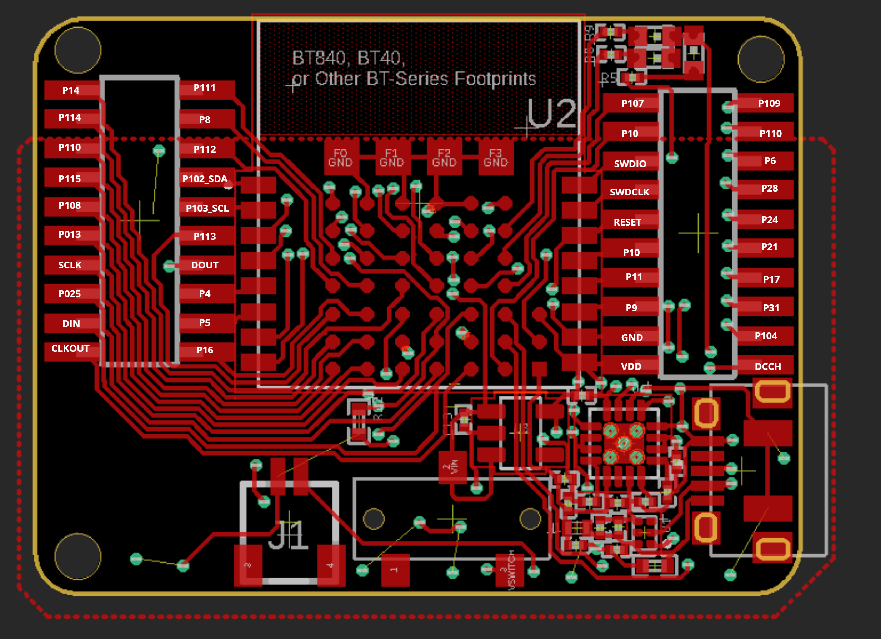
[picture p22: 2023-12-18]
Firmware/nrf5340/BT40PINOUT.PNG

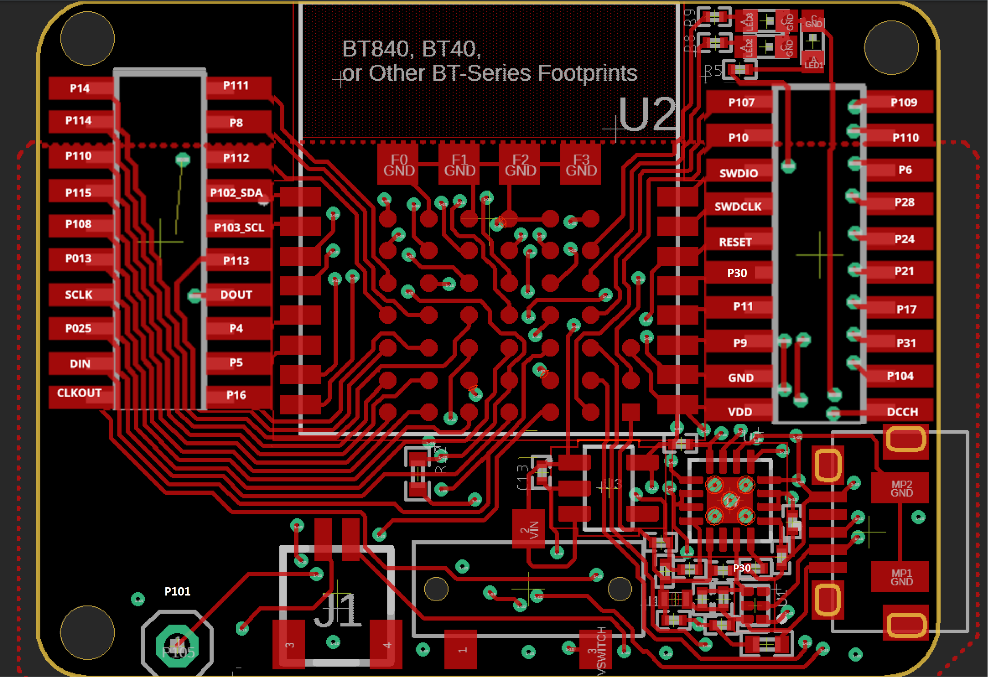
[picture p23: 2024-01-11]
CAD/BT-series/BT40PINOUT.PNG

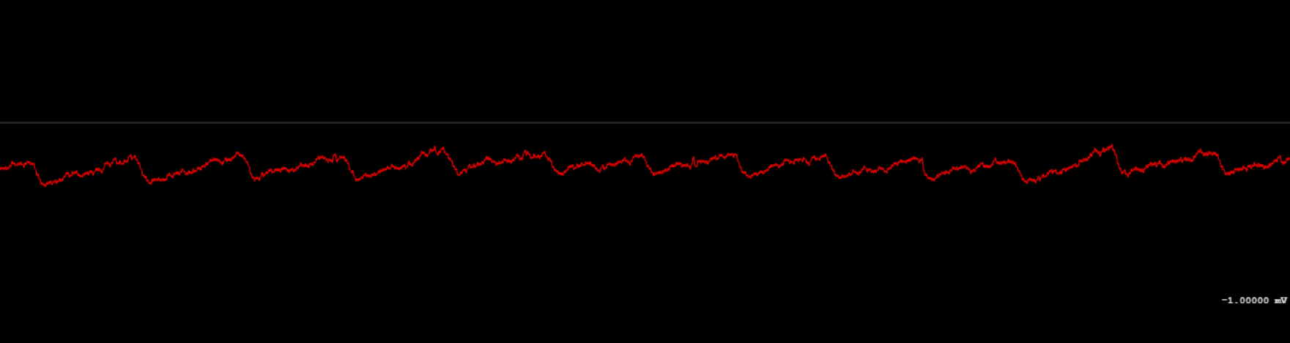
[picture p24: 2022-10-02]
img/PPG_photodiode.png

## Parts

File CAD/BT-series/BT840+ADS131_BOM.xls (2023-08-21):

Designators | Ct | Part # | Description | Substitutes | NOTES | Costs (old) | 1 | 10 | 100 | 1000
U1 | 1 | TPD4S012DRYR (https://www.mouser.com/ProductDetail/Texas-Instruments/TPD4S012DRYR) | TVS Diodes |  |  |  | 0.73 | 6.48 | 49.7 | 314
U2 | 1 | BT40 (https://www.mouser.com/ProductDetail/Fanstel/BT40?qs=zW32dvEIR3ulsM4yjGmroQ==) | Fanstel Microcontroller | BT840, BT832, BT832A, or variants (F, E, X, XE) | Prefer BT40 (nRF53) | From Fanstel: (https://www.fanstel.com/bc840m-compact-nrf52840-module) | 10.41 | 99.8 | 998 | 7650
U3,U4 | 2 | LP5907-3.3MFX (https://www.mouser.com/ProductDetail/Texas-Instruments/LP5907MFX-33-NOPB?qs=biyDIajrTn6NhrJCoL%2FdSQ%3D%3D) | 3v3 LDO | Alt Stock (moq 155) (https://www.win-source.net/texas-instruments-lp5907mfx-3.3nopb.html) |  |  | 0.7 | 5.93 | 41.1 | 269
U5 | 1 | ADS131M08IPBS (https://www.mouser.com/ProductDetail/Texas-Instruments/ADS131M08IPBSR?qs=Cb2nCFKsA8rxAEyQYn%2FiEQ%3D%3D) | ADC 24bit 8ch |  |  | From TI: (https://www.ti.com/product/ADS131M08) | 7.739 | 77.39 | 630.9 | 4206
U6 | 1 | BQ24076RGTR (https://www.mouser.com/ProductDetail/Texas-Instruments/BQ24076RGTR?qs=0lQeLiL1qyaDBd33jHtQfg%3D%3D) | Battery charge/switch interface | BQ2407xRGTR |  |  | 2.52 | 22.7 | 183 | 1250
U7 | 1 | DX4R005JJ2R1800 (https://www.mouser.com/ProductDetail/JAE-Electronics/DX4R005JJ2R1800) | MicroUSB port |  |  |  | 0.79 | 6.32 | 54.9 | 386
S1 | 1 | CL-SB-12B-01T (https://www.mouser.com/ProductDetail/Nidec-Copal/CL-SB-12B-01T) | Switch On-Off | Alt part/source (https://www.aliexpress.com/item/4000930400931.html) |  |  | 0.93 | 8.37 | 66.1 | 533
X1 | 1 | LFXTAL061486Reel (https://www.mouser.com/ProductDetail/IQD/LFXTAL061486Reel) | 8.192Mhz Crystal |  |  |  | 0.92 | 7.63 | 67.5 | 516
X2 | 1 | 830105946101 | 32.7680 Crystal |  |  |  | 0.67 | 6.11 | 52.4 | 524
I1 | 1 | MMZ1005S121CT000 (https://www.mouser.com/ProductDetail/TDK/MMZ1005S121CT000) | 120Ohm/500mAh 0402 INDUCTOR |  |  |  | 0.1 | 0.54 | 2.9 | 23
C1,C2 | 2 | CC0201DRNPO9BN7R0 (https://www.mouser.com/ProductDetail/YAGEO/CC0201DRNPO9BN7R0) | 7pF 0201 MLCC |  |  |  | 0.1 | 0.37 | 1.8 | 10
C3,C4, | 2 | 02015A100JAT2A (https://www.mouser.com/ProductDetail/Kyocera-AVX/02015A100JAT2A?qs=sGAEpiMZZMu2UVWuvJ5cF8J8bUaJvWdoFE9MVTIpUXs%3D) | 10pF 0201 MLCC |  |  |  | 0.1 | 0.37 | 1.8 | 10
C5,C7,C8,C10,C12,C13,C23 | 7 | 02016D224KAT2A (https://www.mouser.com/ProductDetail/Kyocera-AVX/02016D224KAT2A?qs=G2E3TvrFun18LZAcbtmALw%3D%3D) | 1uF 0201 MLCC |  |  |  | 0.1 | 0.37 | 1.8 | 10
C6 | 1 | 02016D224KAT2A (https://www.mouser.com/ProductDetail/Kyocera-AVX/02016D224KAT2A?qs=G2E3TvrFun18LZAcbtmALw%3D%3D) | 220nF 0201 MLCC |  |  |  | 0.1 | 0.37 | 1.8 | 10
C9,C11,C14,C26 | 4 | AMK063EBJ475MP-F (https://www.mouser.com/ProductDetail/Taiyo-Yuden/AMK063EBJ475MP-F?qs=DRkmTr78QAQCUhkfe8WNjg%3D%3D) | 4.7uF 0201 MLCC |  |  |  | 0.1 | 0.37 | 1.8 | 10
C15,C31 | 2 | 0402YG104ZAT4A (https://www.mouser.com/ProductDetail/Kyocera-AVX/0402YG104ZAT4A) | 10uF 0402 MLCC |  |  |  | 0.1 | 0.37 | 1.8 | 10
C18,C22,C27,C30 | 4 | 0201ZD104KAT2A (https://www.mouser.com/ProductDetail/Kyocera-AVX/0201ZD104KAT2A) | 0.1uF 0201 MLCC |  |  |  | 0.1 | 0.37 | 1.8 | 10
C19 | 1 | 0201YD103KAT4A (https://www.mouser.com/ProductDetail/Kyocera-AVX/0201YD103KAT4A) | 10nF 0201 MLCC |  |  |  | 0.1 | 0.37 | 1.8 | 10
C16,C17,C20,C21,C24,C25,C28,C29 | 8 | 02013C101KAT2A (https://www.mouser.com/ProductDetail/KYOCERA-AVX/02013C101KAT2A?qs=hYoCycGuo1kPw8LaKv8JWQ%3D%3D) | 100pF 0201 MLCC |  |  |  | 0.1 | 0.37 | 1.8 | 10
R1 | 1 | CRCW020110K0JNED (https://www.mouser.com/ProductDetail/Vishay-Dale/CRCW020110K0JNED?qs=sGAEpiMZZMskC5GgilGuvpquEUzpanAk) | 10KOhm 0201 RESISTOR |  |  |  | 0.1 | 0.2 | 4.8 | 8
R10, R11 | 2 | AC0402FR-0710KL (https://www.mouser.com/ProductDetail/YAGEO/AC0402FR-0710KL) | 10KOhm 0402 RESISTOR |  |  |  | 0.1 | 0.2 | 4.8 | 8
R2 | 1 | CRCW0201100KFNED (https://www.mouser.com/ProductDetail/Vishay-Dale/CRCW0201100KFNED?qs=sGAEpiMZZMuJrIgwi0BoMbsVWIAikFws) | 100KOhm 0201 RESISTOR |  |  |  | 0.1 | 0.2 | 4.8 | 8
R12,R13 | 2 | AC0402FR-13100KL (https://www.mouser.com/ProductDetail/YAGEO/AC0402FR-13100KL) | 100KOhm 0402 RESISTOR |  |  |  | 0.1 | 0.2 | 4.8 | 8
R6 | 1 | RC0201FR-07348KL (https://www.mouser.com/ProductDetail/YAGEO/RC0201FR-07348KL?qs=Q4gDqC5t5%2FA2a6hJ%252BgV2pg%3D%3D) | 348KOhm 0201 RESISTOR |  |  |  | 0.1 | 0.2 | 4.8 | 8
R7 | 1 | RC0201FR-07750KL (https://www.mouser.com/ProductDetail/YAGEO/RC0201FR-07750KL?qs=Q4gDqC5t5%2FAlI%252BwQIUmARg%3D%3D) | 750KOhm 0201 RESISTOR |  |  |  | 0.1 | 0.2 | 4.8 | 8
R5,R8,R9 | 3 | RC0201FR-073K3L (https://www.mouser.com/ProductDetail/YAGEO/RC0201FR-073K3L?qs=sGAEpiMZZMtJuH53xR2FXAFPwdcdmzLA) | 3.3KOhm 0201 RESISTOR |  |  |  | 0.1 | 0.2 | 4.8 | 8
R3 | 1 | RC0201FR-071K18L (https://www.mouser.com/ProductDetail/YAGEO/RC0201FR-071K18L) | 1.18KOhm 0201 RESISTOR |  |  |  | 0.1 | 0.2 | 4.8 | 8
R4 | 1 | ERJ-1GNF1131C (https://www.mouser.com/ProductDetail/Panasonic/ERJ-1GNF1131C) | 1.13KOhm 0201 RESISTOR |  |  |  | 0.1 | 0.2 | 4.8 | 8
X5 | 1 | NPTC082KFMS-RC (https://www.digikey.com/en/products/detail/sullins-connector-solutions/NPTC082KFMS-RC/776137) | 2X8 SMT 1.25MM HEADER FEMALE |  |  |  | 1.89 | 16.41 | 146.66 | 1047.6
X3,X4 | 2 | NPTC102KFMS-RC (https://www.digikey.com/en/products/detail/sullins-connector-solutions/NPTC102KFMS-RC/776139) | 2X10 SMT 1.25MM HEADER FEMALE
LED1 | 1 | AA1608SESK (https://www.mouser.com/ProductDetail/Kingbright/AA1608SESK) | 0603 CHIPLED ORANGE |  |  |  | 0.48 | 2.81 | 16.2 | 127
LED2 | 1 | AA1608QBS/D-10MAV (https://www.mouser.com/ProductDetail/Kingbright/AA1608QBS-D-10MAV) | 0603 CHIPLED BLUE |  |  |  | 0.48 | 2.81 | 16.2 | 127
LED3 | 1 | AA1608ZGSK-10MAV (https://www.mouser.com/ProductDetail/Kingbright/AA1608ZGSK-10MAV) | 0603 CHIPLED GREEN |  |  |  | 0.46 | 2.96 | 22.8 | 151
J1 | 1 | SM02B-SRSS-TB(LF)(SN) (https://www.mouser.com/ProductDetail/JST/GSM02B-SRSS-TB-LFSNP) | CONN HEADER SH 2POS 1MM
total | 62 |  |  |  |  |  | 30.619 | 271.39 | 2407.76 | 17285.6
 |  |  | CONN HOUSING JST-SH 2POS 1MM | Stock? or Stock? (https://www.tlcelectronics.com/tlc-3789.html) |  | Unit Cost | 30.619 | 27.139 | 24.0776 | 17.2856
 |  |  |  |  |  | W/out headers | 28.729 | 254.98 | 2261.1 | 16238
 |  |  |  |  |  | Unit Cost | 28.729 | 25.498 | 22.611 | 16.238
 |  |  |  |  |  | Does not include battery,and peripherals

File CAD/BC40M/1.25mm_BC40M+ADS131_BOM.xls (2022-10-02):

Designators | Ct | Part # | Description | Substitutes | Cost | 1 | 10 | 100 | 1000
U6 | 1 | TPD4S012DRYR (https://www.mouser.com/ProductDetail/Texas-Instruments/TPD4S012DRYR) | TVS Diodes |  |  | 0.73 | 6.48 | 49.7 | 314
U2 | 1 | BC40M (https://www.mouser.com/ProductDetail/Fanstel/BC40M?qs=Rp5uXu7WBW9BGKNEzxvGRg%3D%3D) | Fanstel Microcontroller | BC40, BC40P | From Fanstel: (https://www.fanstel.com/bc840m-compact-nrf52840-module) | 8.86 | 84.9 | 812 | 7380
U1,U3 | 2 | LP5907-3.3MFX (https://www.mouser.com/ProductDetail/Texas-Instruments/LP5907MFX-33-NOPB?qs=biyDIajrTn6NhrJCoL%2FdSQ%3D%3D) | 3v3 LDO | Stock (moq 155) (https://www.win-source.net/texas-instruments-lp5907mfx-3.3nopb.html) |  | 0.7 | 5.93 | 41.1 | 269
U4 | 1 | ADS131M08IPBS (https://www.mouser.com/ProductDetail/Texas-Instruments/ADS131M08IPBSR?qs=Cb2nCFKsA8rxAEyQYn%2FiEQ%3D%3D) | ADC 24bit 8ch |  | From TI: (https://www.ti.com/product/ADS131M08) | 7.739 | 77.39 | 630.9 | 4206
U5 | 1 | BQ24076RGTR (https://www.mouser.com/ProductDetail/Texas-Instruments/BQ24076RGTR?qs=0lQeLiL1qyaDBd33jHtQfg%3D%3D) | Battery charge/switch interface | BQ2407xRGTR |  | 2.52 | 22.7 | 183 | 1250
U2 | 1 | DX4R005JJ2R1800 (https://www.mouser.com/ProductDetail/JAE-Electronics/DX4R005JJ2R1800) | MicroUSB port |  |  | 0.79 | 6.32 | 54.9 | 386
S1 | 1 | CL-SB-12B-01T (https://www.mouser.com/ProductDetail/Nidec-Copal/CL-SB-12B-01T) | Switch On-Off | Alt part/source (https://www.aliexpress.com/item/4000930400931.html) |  | 0.93 | 8.37 | 66.1 | 533
X1 | 1 | LFXTAL061486Reel (https://www.mouser.com/ProductDetail/IQD/LFXTAL061486Reel) | 8.192Mhz Crystal |  |  | 0.92 | 7.63 | 67.5 | 516
I1 | 1 | MMZ1005S121CT000 (https://www.mouser.com/ProductDetail/TDK/MMZ1005S121CT000) | 120Ohm/500mAh 0402 INDUCTOR |  |  | 0.1 | 0.54 | 2.9 | 23
C1,C2 | 2 | 02015A100JAT2A (https://www.mouser.com/ProductDetail/Kyocera-AVX/02015A100JAT2A?qs=sGAEpiMZZMu2UVWuvJ5cF8J8bUaJvWdoFE9MVTIpUXs%3D) | 10pF 0201 MLCC |  |  | 0.1 | 0.37 | 1.8 | 10
C3, C5, C6, C7, C8, C10, C24 | 7 | 02016D224KAT2A (https://www.mouser.com/ProductDetail/Kyocera-AVX/02016D224KAT2A?qs=G2E3TvrFun18LZAcbtmALw%3D%3D) | 1uF 0201 MLCC |  |  | 0.1 | 0.37 | 1.8 | 10
C4 | 1 | 02016D224KAT2A (https://www.mouser.com/ProductDetail/Kyocera-AVX/02016D224KAT2A?qs=G2E3TvrFun18LZAcbtmALw%3D%3D) | 220nF 0201 MLCC |  |  | 0.1 | 0.37 | 1.8 | 10
C11, C12, C25, C26 | 4 | AMK063EBJ475MP-F (https://www.mouser.com/ProductDetail/Taiyo-Yuden/AMK063EBJ475MP-F?qs=DRkmTr78QAQCUhkfe8WNjg%3D%3D) | 4.7uF 0201 MLCC |  |  | 0.1 | 0.37 | 1.8 | 10
C9, C29 | 2 | 0402YG104ZAT4A (https://www.mouser.com/ProductDetail/Kyocera-AVX/0402YG104ZAT4A) | 10uF 0402 MLCC |  |  | 0.1 | 0.37 | 1.8 | 10
C21, C23, C27, C28 | 4 | 0201ZD104KAT2A (https://www.mouser.com/ProductDetail/Kyocera-AVX/0201ZD104KAT2A) | 0.1uF 0201 MLCC |  |  | 0.1 | 0.37 | 1.8 | 10
C22 | 1 | 0201YD103KAT4A (https://www.mouser.com/ProductDetail/Kyocera-AVX/0201YD103KAT4A) | 10nF 0201 MLCC |  |  | 0.1 | 0.37 | 1.8 | 10
C13, C14, C15, C16, C17, C18, C19, C20 | 8 | 02013C101KAT2A (https://www.mouser.com/ProductDetail/KYOCERA-AVX/02013C101KAT2A?qs=hYoCycGuo1kPw8LaKv8JWQ%3D%3D) | 100pF 0201 MLCC | 1uF 0201 MLCC |  | 0.1 | 0.37 | 1.8 | 10
R27 | 1 | CRCW020110K0JNED (https://www.mouser.com/ProductDetail/Vishay-Dale/CRCW020110K0JNED?qs=sGAEpiMZZMskC5GgilGuvpquEUzpanAk) | 10KOhm 0201 RESISTOR |  |  | 0.1 | 0.2 | 4.8 | 8
R27, R28 | 2 | AC0402FR-0710KL (https://www.mouser.com/ProductDetail/YAGEO/AC0402FR-0710KL) | 10KOhm 0402 RESISTOR |  |  | 0.1 | 0.2 | 4.8 | 8
R24 | 1 | CRCW0201100KFNED (https://www.mouser.com/ProductDetail/Vishay-Dale/CRCW0201100KFNED?qs=sGAEpiMZZMuJrIgwi0BoMbsVWIAikFws) | 100KOhm 0201 RESISTOR |  |  | 0.1 | 0.2 | 4.8 | 8
R30,R31 | 2 | AC0402FR-13100KL (https://www.mouser.com/ProductDetail/YAGEO/AC0402FR-13100KL) | 100KOhm 0402 RESISTOR |  |  | 0.1 | 0.2 | 4.8 | 8
R22 | 1 | RC0201FR-07348KL (https://www.mouser.com/ProductDetail/YAGEO/RC0201FR-07348KL?qs=Q4gDqC5t5%2FA2a6hJ%252BgV2pg%3D%3D) | 348KOhm 0201 RESISTOR |  |  | 0.1 | 0.2 | 4.8 | 8
R23 | 1 | RC0201FR-07750KL (https://www.mouser.com/ProductDetail/YAGEO/RC0201FR-07750KL?qs=Q4gDqC5t5%2FAlI%252BwQIUmARg%3D%3D) | 750KOhm 0201 RESISTOR |  |  | 0.1 | 0.2 | 4.8 | 8
R1, R2, R3, R26 | 3 | RC0201FR-073K3L (https://www.mouser.com/ProductDetail/YAGEO/RC0201FR-073K3L?qs=sGAEpiMZZMtJuH53xR2FXAFPwdcdmzLA) | 3.3KOhm 0201 RESISTOR |  |  | 0.1 | 0.2 | 4.8 | 8
R4 | 1 | RC0201FR-071K18L (https://www.mouser.com/ProductDetail/YAGEO/RC0201FR-071K18L) | 1.18KOhm 0201 RESISTOR |  |  | 0.1 | 0.2 | 4.8 | 8
R5 | 1 | ERJ-1GNF1131C (https://www.mouser.com/ProductDetail/Panasonic/ERJ-1GNF1131C) | 1.13KOhm 0201 RESISTOR |  |  | 0.1 | 0.2 | 4.8 | 8
R25 | 1 | RC0805JR-070RL (https://www.mouser.com/ProductDetail/YAGEO/RC0805JR-070RL?qs=sGAEpiMZZMudkDON%252B1gPs8OLkr0oi8sC) | 0Ohm 0805 RESISTOR |  |  | 0.1 | 0.2 | 4.8 | 8
JP1 | 1 | NPTC082KFMS-RC (https://www.digikey.com/en/products/detail/sullins-connector-solutions/NPTC082KFMS-RC/776137) | 2X8 SMT 1.25MM HEADER FEMALE |  |  | 3.75 | 36 | 300 | 2170
JP2,JP3 | 2 | NPTC102KFMS-RC (https://www.digikey.com/en/products/detail/sullins-connector-solutions/NPTC102KFMS-RC/776139) | 2X10 SMT 1.25MM HEADER FEMALE |  |  | 4.12 | 39.6 | 330 | 2390
LED1 | 1 | L1MC-RGB0028000MP0 (https://www.mouser.com/ProductDetail/Lumileds/L1MC-RGB0028000MP0) | 3258 RGB LED |  |  | 0.48 | 2.81 | 16.2 | 127
LED2 | 1 | AA1608QBS/D-10MAV (https://www.mouser.com/ProductDetail/Kingbright/AA1608QBS-D-10MAV) | 0603 CHIPLED BLUE |  |  | 0.48 | 2.81 | 16.2 | 127
J1 | 1 | SM02B-SRSS-TB(LF)(SN) (https://www.mouser.com/ProductDetail/JST/GSM02B-SRSS-TB-LFSNP) | CONN HEADER SH 2POS 1MM |  | Win-Source: (moq 135) (https://www.win-source.net/rectangular-connectors-sm02b-srss-tblfsn.html) | 1 | 10 | 51.74 | 301.125
total | 59 |  |  |  |  | 34.919 | 316.44 | 2684.64 | 20152.125
 | N/A | SHR-02V-S (https://www.mouser.com/ProductDetail/JST/DSHR-02V-S-B) | CONN HOUSING JST-SH 2POS 1MM | Stock? or Stock? (https://www.tlcelectronics.com/tlc-3789.html) | Unit Cost | 34.919 | 31.644 | 26.8464 | 20.152125
 |  |  |  |  | W/out headers | 27.049 | 240.84 | 2054.64 | 15592.125
 |  |  |  |  | Unit Cost (not accurate) | 27.049 | 24.084 | 20.5464 | 15.592125

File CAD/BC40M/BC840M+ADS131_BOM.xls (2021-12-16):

Designators | Ct | Part # | Description | Substitutes | Cost | 1 | 10 | 100 | 1000
U1 | 1 | TPD4S012DRYR (https://www.mouser.com/ProductDetail/Texas-Instruments/TPD4S012DRYR) | TVS Diodes |  |  | 0.73 | 6.48 | 49.7 | 314
U2 | 1 | BC840M (https://www.mouser.com/ProductDetail/Fanstel/BC840M) | Fanstel Microcontroller |  | From Fanstel: (https://www.fanstel.com/bc840m-compact-nrf52840-module) | 8.86 | 84.9 | 812 | 7380
U3,U4 | 2 | LP5907-3.3MFX (https://www.mouser.com/ProductDetail/Texas-Instruments/LP5907MFX-33-NOPB?qs=biyDIajrTn6NhrJCoL%2FdSQ%3D%3D) | 3v3 LDO | Stock (moq 155) (https://www.win-source.net/texas-instruments-lp5907mfx-3.3nopb.html) |  | 0.7 | 5.93 | 41.1 | 269
U5 | 1 | ADS131M08IPBS (https://www.mouser.com/ProductDetail/Texas-Instruments/ADS131M08IPBSR?qs=Cb2nCFKsA8rxAEyQYn%2FiEQ%3D%3D) | ADC 24bit 8ch |  | From TI: (https://www.ti.com/product/ADS131M08) | 7.739 | 77.39 | 630.9 | 4206
U6 | 1 | BQ24076RGTR (https://www.mouser.com/ProductDetail/Texas-Instruments/BQ24076RGTR?qs=0lQeLiL1qyaDBd33jHtQfg%3D%3D) | Battery charge/switch interface | BQ2407xRGTR |  | 2.52 | 22.7 | 183 | 1250
U7 | 1 | DX4R005JJ2R1800 (https://www.mouser.com/ProductDetail/JAE-Electronics/DX4R005JJ2R1800) | MicroUSB port |  |  | 0.79 | 6.32 | 54.9 | 386
S1 | 1 | CL-SB-12B-01T (https://www.mouser.com/ProductDetail/Nidec-Copal/CL-SB-12B-01T) | Switch On-Off | Alt part/source (https://www.aliexpress.com/item/4000930400931.html) |  | 0.93 | 8.37 | 66.1 | 533
X1 | 1 | LFXTAL061486Reel (https://www.mouser.com/ProductDetail/IQD/LFXTAL061486Reel) | 8.192Mhz Crystal |  |  | 0.92 | 7.63 | 67.5 | 516
X2 | 1 | 830105946101 | 32.7680 Crystal |  |  | 0.67 | 6.11 | 52.4 | 524
I1 | 1 | MMZ1005S121CT000 (https://www.mouser.com/ProductDetail/TDK/MMZ1005S121CT000) | 120Ohm/500mAh 0402 INDUCTOR |  |  | 0.1 | 0.54 | 2.9 | 23
C1,C2 | 2 | CC0201DRNPO9BN7R0 (https://www.mouser.com/ProductDetail/YAGEO/CC0201DRNPO9BN7R0) | 7pF 0201 MLCC |  |  | 0.1 | 0.37 | 1.8 | 10
C3,C4, | 2 | 02015A100JAT2A (https://www.mouser.com/ProductDetail/Kyocera-AVX/02015A100JAT2A?qs=sGAEpiMZZMu2UVWuvJ5cF8J8bUaJvWdoFE9MVTIpUXs%3D) | 10pF 0201 MLCC |  |  | 0.1 | 0.37 | 1.8 | 10
C5,C7,C8,C10,C12,C13,C23 | 7 | 02016D224KAT2A (https://www.mouser.com/ProductDetail/Kyocera-AVX/02016D224KAT2A?qs=G2E3TvrFun18LZAcbtmALw%3D%3D) | 1uF 0201 MLCC |  |  | 0.1 | 0.37 | 1.8 | 10
C6 | 1 | 02016D224KAT2A (https://www.mouser.com/ProductDetail/Kyocera-AVX/02016D224KAT2A?qs=G2E3TvrFun18LZAcbtmALw%3D%3D) | 220nF 0201 MLCC |  |  | 0.1 | 0.37 | 1.8 | 10
C9,C11,C14,C26 | 4 | AMK063EBJ475MP-F (https://www.mouser.com/ProductDetail/Taiyo-Yuden/AMK063EBJ475MP-F?qs=DRkmTr78QAQCUhkfe8WNjg%3D%3D) | 4.7uF 0201 MLCC |  |  | 0.1 | 0.37 | 1.8 | 10
C15,C31 | 2 | 0402YG104ZAT4A (https://www.mouser.com/ProductDetail/Kyocera-AVX/0402YG104ZAT4A) | 10uF 0402 MLCC |  |  | 0.1 | 0.37 | 1.8 | 10
C18,C22,C27,C30 | 4 | 0201ZD104KAT2A (https://www.mouser.com/ProductDetail/Kyocera-AVX/0201ZD104KAT2A) | 0.1uF 0201 MLCC |  |  | 0.1 | 0.37 | 1.8 | 10
C19 | 1 | 0201YD103KAT4A (https://www.mouser.com/ProductDetail/Kyocera-AVX/0201YD103KAT4A) | 10nF 0201 MLCC |  |  | 0.1 | 0.37 | 1.8 | 10
C16,C17,C20,C21,C24,C25,C28,C29 | 8 | 06035A101JAT4A (https://www.mouser.com/ProductDetail/Kyocera-AVX/06035A101JAT4A?qs=sGAEpiMZZMsSCEehGlfQHcAhveYwxUP%2F) | 100pF 0603 MLCC | 1uF 0603 MLCC |  | 0.1 | 0.37 | 1.8 | 10
R6,R7,R8,R9,R10,R11,R12,R13,R1,R15,R16,R17,R18,R19,R20 | 16 | AC0603JR-071ML (https://www.mouser.com/ProductDetail/YAGEO/AC0603JR-071ML) | 1MOhm 0603 RESISTOR | 100k 0603 RESISTOR |  | 0.1 | 0.2 | 4.8 | 8
R1 | 1 | CRCW020110K0JNED (https://www.mouser.com/ProductDetail/Vishay-Dale/CRCW020110K0JNED?qs=sGAEpiMZZMskC5GgilGuvpquEUzpanAk) | 10KOhm 0201 RESISTOR |  |  | 0.1 | 0.2 | 4.8 | 8
R28, R29 | 2 | AC0402FR-0710KL (https://www.mouser.com/ProductDetail/YAGEO/AC0402FR-0710KL) | 10KOhm 0402 RESISTOR |  |  | 0.1 | 0.2 | 4.8 | 8
R2 | 1 | CRCW0201100KFNED (https://www.mouser.com/ProductDetail/Vishay-Dale/CRCW0201100KFNED?qs=sGAEpiMZZMuJrIgwi0BoMbsVWIAikFws) | 100KOhm 0201 RESISTOR |  |  | 0.1 | 0.2 | 4.8 | 8
R30,R31 | 2 | AC0402FR-13100KL (https://www.mouser.com/ProductDetail/YAGEO/AC0402FR-13100KL) | 100KOhm 0402 RESISTOR |  |  | 0.1 | 0.2 | 4.8 | 8
R23 | 1 | RC0603FR-07348KL (https://www.mouser.com/ProductDetail/YAGEO/RC0603FR-07348KL) | 348KOhm 0603 RESISTOR |  |  | 0.1 | 0.2 | 4.8 | 8
R24 | 1 | CR0603-FX-7503ELF (https://www.mouser.com/ProductDetail/Bourns/CR0603-FX-7503ELF) | 750KOhm 0603 RESISTOR |  |  | 0.1 | 0.2 | 4.8 | 8
R5,R26,R27 | 3 | RC0201FR-073K3L (https://www.mouser.com/ProductDetail/YAGEO/RC0201FR-073K3L?qs=sGAEpiMZZMtJuH53xR2FXAFPwdcdmzLA) | 3.3KOhm 0201 RESISTOR |  |  | 0.1 | 0.2 | 4.8 | 8
R3 | 1 | RC0603FR-071K18L (https://www.mouser.com/ProductDetail/YAGEO/RC0603FR-071K18L) | 1.18KOhm 0603 RESISTOR |  |  | 0.1 | 0.2 | 4.8 | 8
R4 | 1 | CR0603-FX-1131ELF (https://www.mouser.com/ProductDetail/Bourns/CR0603-FX-1131ELF?qs=sGAEpiMZZMtlubZbdhIBIJoX7P5Bll7anIOIKGY9fwQ%3D) | 1.13KOhm 0603 RESISTOR |  |  | 0.1 | 0.2 | 4.8 | 8
R22,R25 | 2 | RC0805JR-070RL (https://www.mouser.com/ProductDetail/YAGEO/RC0805JR-070RL?qs=sGAEpiMZZMudkDON%252B1gPs8OLkr0oi8sC) | 0Ohm 0805 RESISTOR |  |  | 0.1 | 0.2 | 4.8 | 8
JP1 | 1 | SSM-108-F-DV-K-TR (https://www.mouser.com/ProductDetail/Samtec/SSM-108-F-DV-K-TR?qs=%252BZP6%2F%252BtExtDuuLV%2Fw6Rg7w%3D%3D) | 2X8 SMT 2.54MM HEADER FEMALE |  |  | 3.75 | 36 | 300 | 2170
JP2,JP3 | 2 | SSM-110-F-DV-P-TR (https://www.mouser.com/ProductDetail/Samtec/SSM-110-F-DV-P-TR?qs=rU5fayqh%252BE3TqvVcljjong%3D%3D) | 2X10 SMT 2.54MM HEADER FEMALE |  |  | 4.12 | 39.6 | 330 | 2390
LED1 | 1 | AA1608SESK (https://www.mouser.com/ProductDetail/Kingbright/AA1608SESK) | 0603 CHIPLED ORANGE |  |  | 0.48 | 2.81 | 16.2 | 127
LED2 | 1 | AA1608QBS/D-10MAV (https://www.mouser.com/ProductDetail/Kingbright/AA1608QBS-D-10MAV) | 0603 CHIPLED BLUE |  |  | 0.48 | 2.81 | 16.2 | 127
LED3 | 1 | AA1608ZGSK-10MAV (https://www.mouser.com/ProductDetail/Kingbright/AA1608ZGSK-10MAV) | 0603 CHIPLED GREEN |  |  | 0.46 | 2.96 | 22.8 | 151
J1 | 1 | SM02B-SRSS-TB(LF)(SN) (https://www.mouser.com/ProductDetail/JST/GSM02B-SRSS-TB-LFSNP) | CONN HEADER SH 2POS 1MM |  | Win-Source: (moq 135) (https://www.win-source.net/rectangular-connectors-sm02b-srss-tblfsn.html) | 1 | 10 | 51.74 | 301.125
total | 80 |  |  |  |  | 36.249 | 326.08 | 2766.44 | 20845.125
 | N/A | SHR-02V-S (https://www.mouser.com/ProductDetail/JST/DSHR-02V-S-B) | CONN HOUSING SH 2POS 1MM | Stock? or Stock? (https://www.tlcelectronics.com/tlc-3789.html) | Unit Cost | 36.249 | 32.608 | 27.6644 | 20.845125
 |  |  |  |  | W/out headers | 28.379 | 250.48 | 2136.44 | 16285.125
 |  |  |  |  | Unit Cost (not accurate) | 28.379 | 25.048 | 21.3644 | 16.285125

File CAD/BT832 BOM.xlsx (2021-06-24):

Part | Des | Qty | Desc | Alt | Notes | US Mouser prices | 1 | 10 | 100 | 1000 |  | 5 Assembled Turnkey Quote (China prices) | 5sets | Total Cost | Note | Part | Des
BT832A (https://www.mouser.com/ProductDetail/Fanstel/BT832A) | U2 | 1 | BLE + CortexM4/M4F |  |  | The higher priced chips are cheaper from the manufacturer | 7.33 | 67.3 | 550 | 3920 | 3.75 ea on Fanstel |  | $10.92 | $54.60 | 7-10work days | BT832A | U2
CP2102N-A02-GQFN20R (https://www.mouser.com/ProductDetail/Silicon-Labs/CP2102N-A02-GQFN20R) | IC1 | 1 | USB-UART |  |  |  | 1.85 | 17.6 | 155 | 1390 |  |  | $3.99 | $19.95 | CP2102-GMR QFN-28 | CP2102 | IC1 | Incorrect PN
DX4R005JJ2R1800 (https://www.mouser.com/ProductDetail/JAE-Electronics/DX4R005JJ2R1800) | MicroUSB | 1 | MicroUSB Port |  |  |  | 0.79 | 6.32 | 54.9 | 386 |  |  | $1.16 | $5.78 | 7-10work days | DX4R005JJ2R1800 | MicroUSB
ADS131M08IPBS (https://www.mouser.com/ProductDetail/Texas-Instruments/ADS131M08IPBSR?qs=Cb2nCFKsA8rxAEyQYn%2FiEQ%3D%3D) | U5 | 1 | ADC 24bit 8ch |  |  |  | 8.04 | 72.7 | 611 | 4.98 |  |  | $11.55 | $57.75 | 7-10work days | ADS131M08IPBS | U5
LP5907-3.3MFX (https://www.mouser.com/ProductDetail/Texas-Instruments/LP5907MFX-33-NOPB?qs=biyDIajrTn6NhrJCoL%2FdSQ%3D%3D) | U3,U4 | 2 | 3.3V LDO |  |  |  | 0.63 | 5.37 | 37.2 | 244 |  |  | $1.05 | $10.50 | LP5907MFX-3.3/NOPB | LP5907-3.3MFX (https://www.mouser.com/ProductDetail/Texas-Instruments/LP5907MFX-33-NOPB?qs=biyDIajrTn6NhrJCoL%2FdSQ%3D%3D) | U3,U4
830050789 (https://www.mouser.com/ProductDetail/Wurth-Elektronik/830050789?qs=2WXlatMagcG%2Fhb4pC63Fuw%3D%3D) | X2 | 1 | 32.7680kHz XTAL |  |  |  | 0.68 | 5.67 | 50.1 | 384 |  |  | $0.94 | $4.72 | 7-10work days | 830050789 | X2
LFXTAL061486Reel (https://www.mouser.com/ProductDetail/IQD/LFXTAL061486Reel) | X1 | 1 | 8.192MHz XTAL | 830061486 (https://www.mouser.com/ProductDetail/Wurth-Elektronik/830061486) |  |  | 0.76 | 6.38 | 56.4 | 432 |  |  | $1.05 | $5.25 | LFXTAL061486Reel 7-10work days ok or not | LFXTAL061486Reel (https://www.mouser.com/ProductDetail/IQD/LFXTAL061486Reel) | X1
GCM1555C1H100JA16D (https://www.mouser.com/ProductDetail/Murata-Electronics/GCM1555C1H100JA16D) | C3,C4 | 2 | 10pF Cap | 0402 SMD Caps. | For 8.192MHz XTAL |  | 0.12 | 0.59 | 2.6 | 17 |  |  | $0.05 | $0.53 |  | GCM1555C1H100JA16D (https://www.mouser.com/ProductDetail/Murata-Electronics/GCM1555C1H100JA16D) | C3,C4
UMK105CG120JV-F (https://www.mouser.com/ProductDetail/Taiyo-Yuden/UMK105CG120JV-F?qs=PzICbMaShUf1UpWoIX7W8g%3D%3D) | C1,C2 | 2 | 12pF Cap | 0402 SMD Caps. | For 32KHz XTAL |  | 0.1 | 0.29 | 1.5 | 8 |  |  | $0.05 | $0.53 |  | UMK105CG120JV-F (https://www.mouser.com/ProductDetail/Taiyo-Yuden/UMK105CG120JV-F?qs=PzICbMaShUf1UpWoIX7W8g%3D%3D) | C1,C2
TMK105BJ104KV-F (https://www.mouser.com/ProductDetail/Taiyo-Yuden/TMK105BJ104KV-F?qs=PzICbMaShUcuRhf9Ji%2F5mA%3D%3D) | C11 | 1 | 0.1uF Cap | 0402 SMD Caps. |  |  | 0.1 | 0.34 | 2 | 11 |  |  | $0.10 | $0.53 |  | TMK105BJ104KV-F (https://www.mouser.com/ProductDetail/Taiyo-Yuden/TMK105BJ104KV-F?qs=PzICbMaShUcuRhf9Ji%2F5mA%3D%3D) | C11
JMK105BJ105KV-F (https://www.mouser.com/ProductDetail/Taiyo-Yuden/JMK105BJ105KV-F?qs=I6KAKw0tg2yJ6Hx%2Fbib9CA%3D%3D) | C5,C7,C8,C10,C12,C13 | 6 | 1uF Cap | 0402 SMD Caps. |  |  | 0.1 | 0.37 | 1.6 | 9 |  |  | $0.10 | $3.15 |  | JMK105BJ105KV-F (https://www.mouser.com/ProductDetail/Taiyo-Yuden/JMK105BJ105KV-F?qs=I6KAKw0tg2yJ6Hx%2Fbib9CA%3D%3D) | C5,C7,C8,C10,C12,C13
06033C224KAT2A (https://www.mouser.com/ProductDetail/AVX/06033C224KAT2A/?qs=%2FcnINApUglM4zoxC%252BAA4%252BQ%3D%3D) | C6 | 1 | 220uF Cap | 0402 SMD Caps. |  |  | 0.19 | 1.25 | 6.6 | 40 |  |  | $0.10 | $0.53 | offer part 220nF | 06033C224KAT2A (https://www.mouser.com/ProductDetail/AVX/06033C224KAT2A/?qs=%2FcnINApUglM4zoxC%252BAA4%252BQ%3D%3D) | C6
C0603C104J4REC7411 (https://www.mouser.com/ProductDetail/KEMET/C0603C104J4REC7411/) | C9 | 1 | 100uF Cap | 0402 SMD Caps. |  |  | 0.19 | 1.12 | 6 | 40 |  |  | $0.53 | $2.62 | offer part 100nF 7-10work days | C0603C104J4REC7411 (https://www.mouser.com/ProductDetail/KEMET/C0603C104J4REC7411/) | C9
GRM155R60J106ME05D (https://www.mouser.com/ProductDetail/Murata-Electronics/GRM155R60J106ME05D) | C15 | 1 | 10uF Cap | 0402 SMD Caps. |  |  | 0.19 | 1.12 | 6 | 40 |  |  | $0.21 | $1.05 |  | GRM155R60J106ME05D (https://www.mouser.com/ProductDetail/Murata-Electronics/GRM155R60J106ME05D) | C15
JMK105BBJ475MV8F (https://www.mouser.com/ProductDetail/Taiyo-Yuden/JMK105BBJ475MV8F) | C16,C17 | 2 | 4.7uF Cap | 0402 SMD Caps. |  |  | 0.19 | 0.76 | 5.2 | 38 |  |  | $0.10 | $1.05 |  | JMK105BBJ475MV8F (https://www.mouser.com/ProductDetail/Taiyo-Yuden/JMK105BBJ475MV8F) | C16,C17
ERJ-2GEJ332X (https://www.mouser.com/ProductDetail/Panasonic/ERJ-2GEJ332X?qs=YMBIwoNQYdWpAbrP4mVohA%3D%3D) | R1,R2 | 2 | 3.3kΩ | 0402 SMD Res. |  |  | 0.1 | 0.19 | 1 | 4 |  |  | $0.05 | $0.53 |  | ERJ-2GEJ332X (https://www.mouser.com/ProductDetail/Panasonic/ERJ-2GEJ332X?qs=YMBIwoNQYdWpAbrP4mVohA%3D%3D) | R1,R2
RC0402FR-0710KL (https://www.mouser.com/ProductDetail/Yageo/RC0402FR-0710KL?qs=I1mnnYJTTsxUoNwrUsQExA%3D%3D) | R3,R6 | 2 | 10kΩ | 0402 SMD Res. |  |  | 0.1 | 0.14 | 0.5 | 3 |  |  | $0.05 | $0.53 |  | RC0402FR-0710KL (https://www.mouser.com/ProductDetail/Yageo/RC0402FR-0710KL?qs=I1mnnYJTTsxUoNwrUsQExA%3D%3D) | R3,R6
ERJ-2GEJ473X (https://www.mouser.com/ProductDetail/Panasonic/ERJ-2GEJ473X) | R4 | 1 | 47kΩ | 0402 SMD Res. |  |  | 0.1 | 0.22 | 0.9 | 5 |  |  | $0.05 | $0.26 |  | ERJ-2GEJ473X (https://www.mouser.com/ProductDetail/Panasonic/ERJ-2GEJ473X) | R4
ERJ-2RKF2001X (https://www.mouser.com/ProductDetail/Panasonic/ERJ-2RKF2001X?qs=H7k1u0Mp9JSbtBe1nkwQGA%3D%3D) | R5 | 1 | 2kΩ | 0402 SMD Res. |  |  | 0.1 | 0.22 | 0.9 | 4 |  |  | $0.05 | $0.26 |  | ERJ-2RKF2001X (https://www.mouser.com/ProductDetail/Panasonic/ERJ-2RKF2001X?qs=H7k1u0Mp9JSbtBe1nkwQGA%3D%3D) | R5
JST-PH 2.0MM SMT (https://www.mouser.com/ProductDetail/Adafruit/1769?qs=GURawfaeGuBbgoGtf2XstA%3D%3D) | J1 | 1 | LiPo Battery Plug |  | Use Ebay bulk or aliexpress |  | 0.75 | 6 | 11 | 100 |  |  | $1.05 | $5.25 | J1 485-1769 5PCS $1.05/PCS 7-10WORK DAYS | JST-PH 2.0MM SMT | J1
MCP73831T-5ACI/MC (https://www.mouser.com/ProductDetail/Microchip-Technology/MCP73831T-5ACI-MC?qs=hH%252BOa0VZEiCKvIDhidFX4A%3D%3D) | U1 | 1 | Battery regulator |  |  |  | 0.66 | 6.6 | 54.6 | 540.6 |  |  | $1.26 | $6.30 | MCP73831T-2ACI/OT SOT23-5 ok or not | MCP73831T | U1
BCM857BS-7-F (https://www.mouser.com/ProductDetail/Diodes-Incorporated/BCM857BS-7-F?qs=60RJRzIpcl83Pda4UUWqGw%3D%3D) | U6 | 1 | Bipolar Transistor |  |  |  | 0.31 | 2.57 | 13.6 | 61 |  |  | $0.53 | $2.62 | 7-10work days | BCM857BS-7-F | U6
B5817WS-TP (https://www.mouser.com/ProductDetail/Micro-Commercial-Components-MCC/B5817WS-TP) | D1 | 1 | Schottkey Diode |  |  |  | 0.44 | 3.34 | 19 | 97 |  |  | $0.10 | $0.53 |  | B5817WS | D1
BAT1000-7-F (https://www.mouser.com/ProductDetail/Diodes-Incorporated/BAT1000-7-F) | D2,D3 | 2 | Dual Schottkey Diodes |  | ??? |  | 0.57 | 4.95 | 37 | 225 |  |  | $0.21 | $2.10 |  | BAT1000-7-F | D2,D3
155060BS75300 (https://www.mouser.com/ProductDetail/Wurth-Elektronik/155060BS75300?qs=GedFDFLaBXFE8klTFAyuFA%3D%3D) | LED1,LED2 | 2 | Indicator LED 0603 |  |  |  | 0.39 | 3.22 | 25.8 | 214 |  |  | $0.73 | $7.35 | 7-10work days | 155060BS75300 (https://www.mouser.com/ProductDetail/Wurth-Elektronik/155060BS75300?qs=GedFDFLaBXFE8klTFAyuFA%3D%3D) | LED1,LED2
CL-SB-12B-01T (https://www.mouser.com/ProductDetail/Nidec-Copal/CL-SB-12B-01T) | S1 | 1 | Switch On-Off |  |  |  | 0.93 | 8.37 | 66.1 | 533 |  |  | $3.15 | $15.75 | 2-3 weeks | CL-SB-12B-01T | S1
 |  | 39 |  |  |  | Totals: | 25.71 | 223 | 1776.5 | 8750.58 |  |  |  | $210.00
 |  |  |  |  |  |  |  |  |  |  |  |  |  | $311 w/ assembly
 |  |  |  |  |  |  |  |  |  |  |  |  |  | $30 Shipping

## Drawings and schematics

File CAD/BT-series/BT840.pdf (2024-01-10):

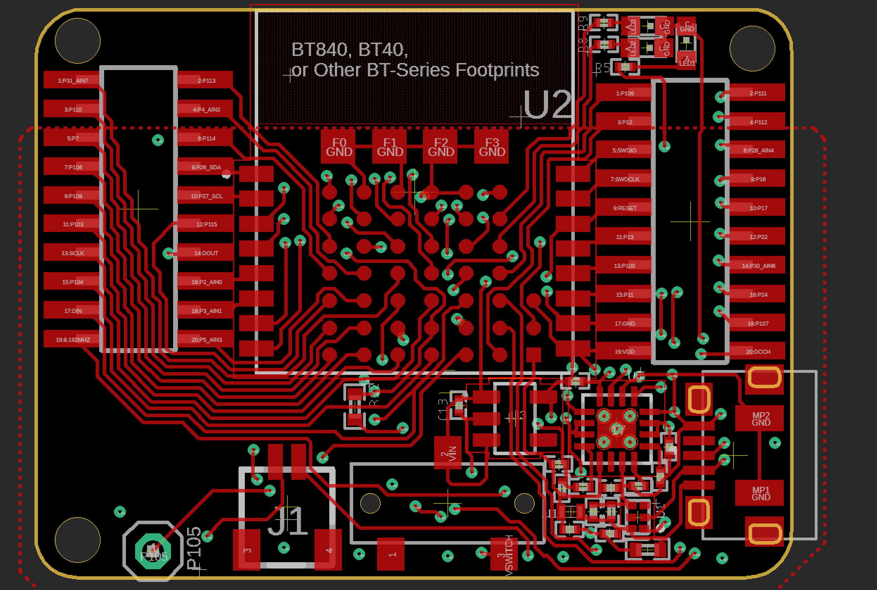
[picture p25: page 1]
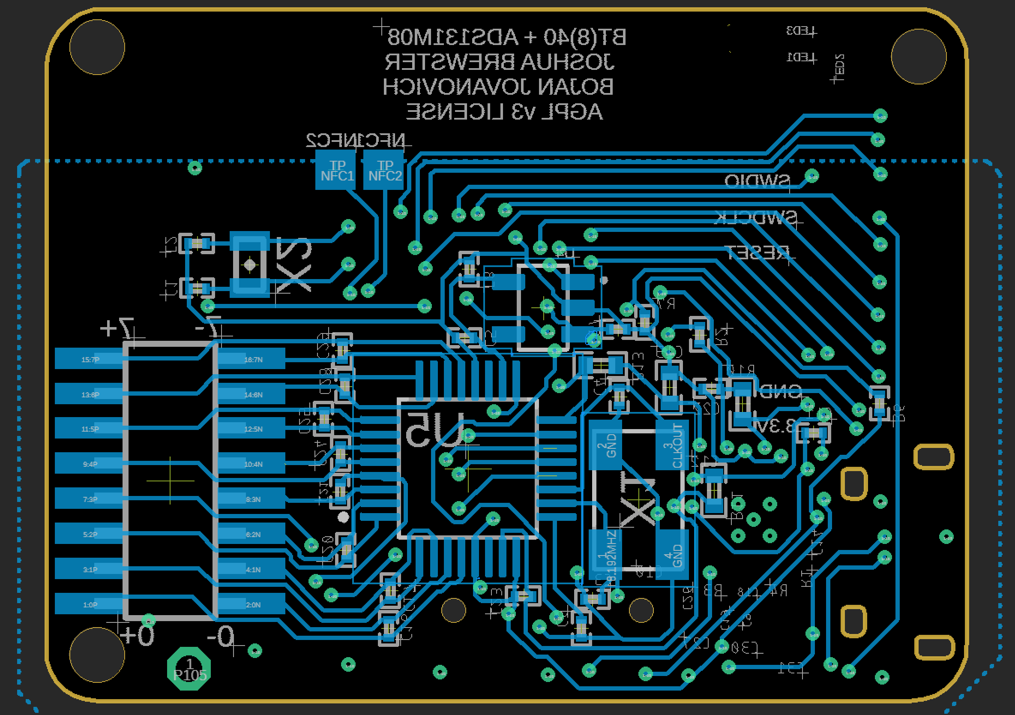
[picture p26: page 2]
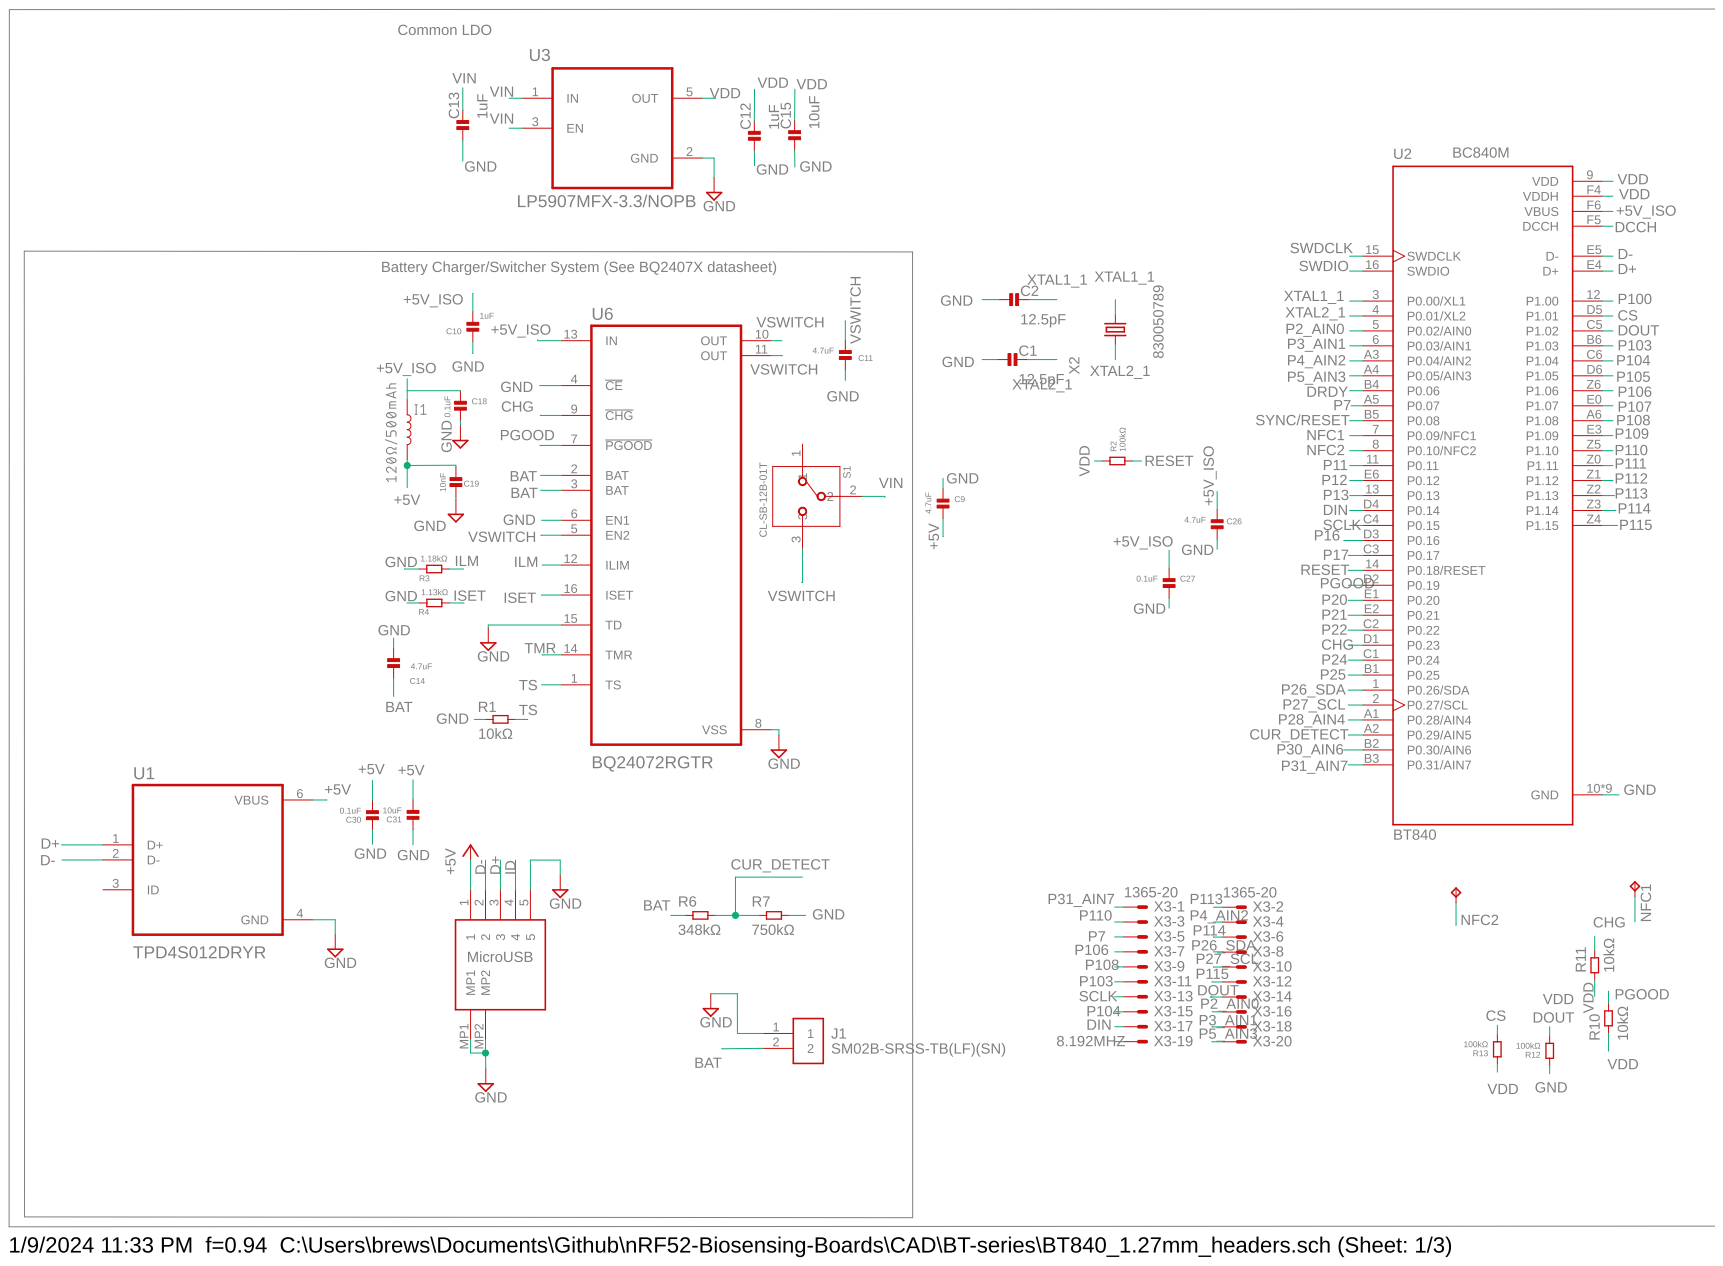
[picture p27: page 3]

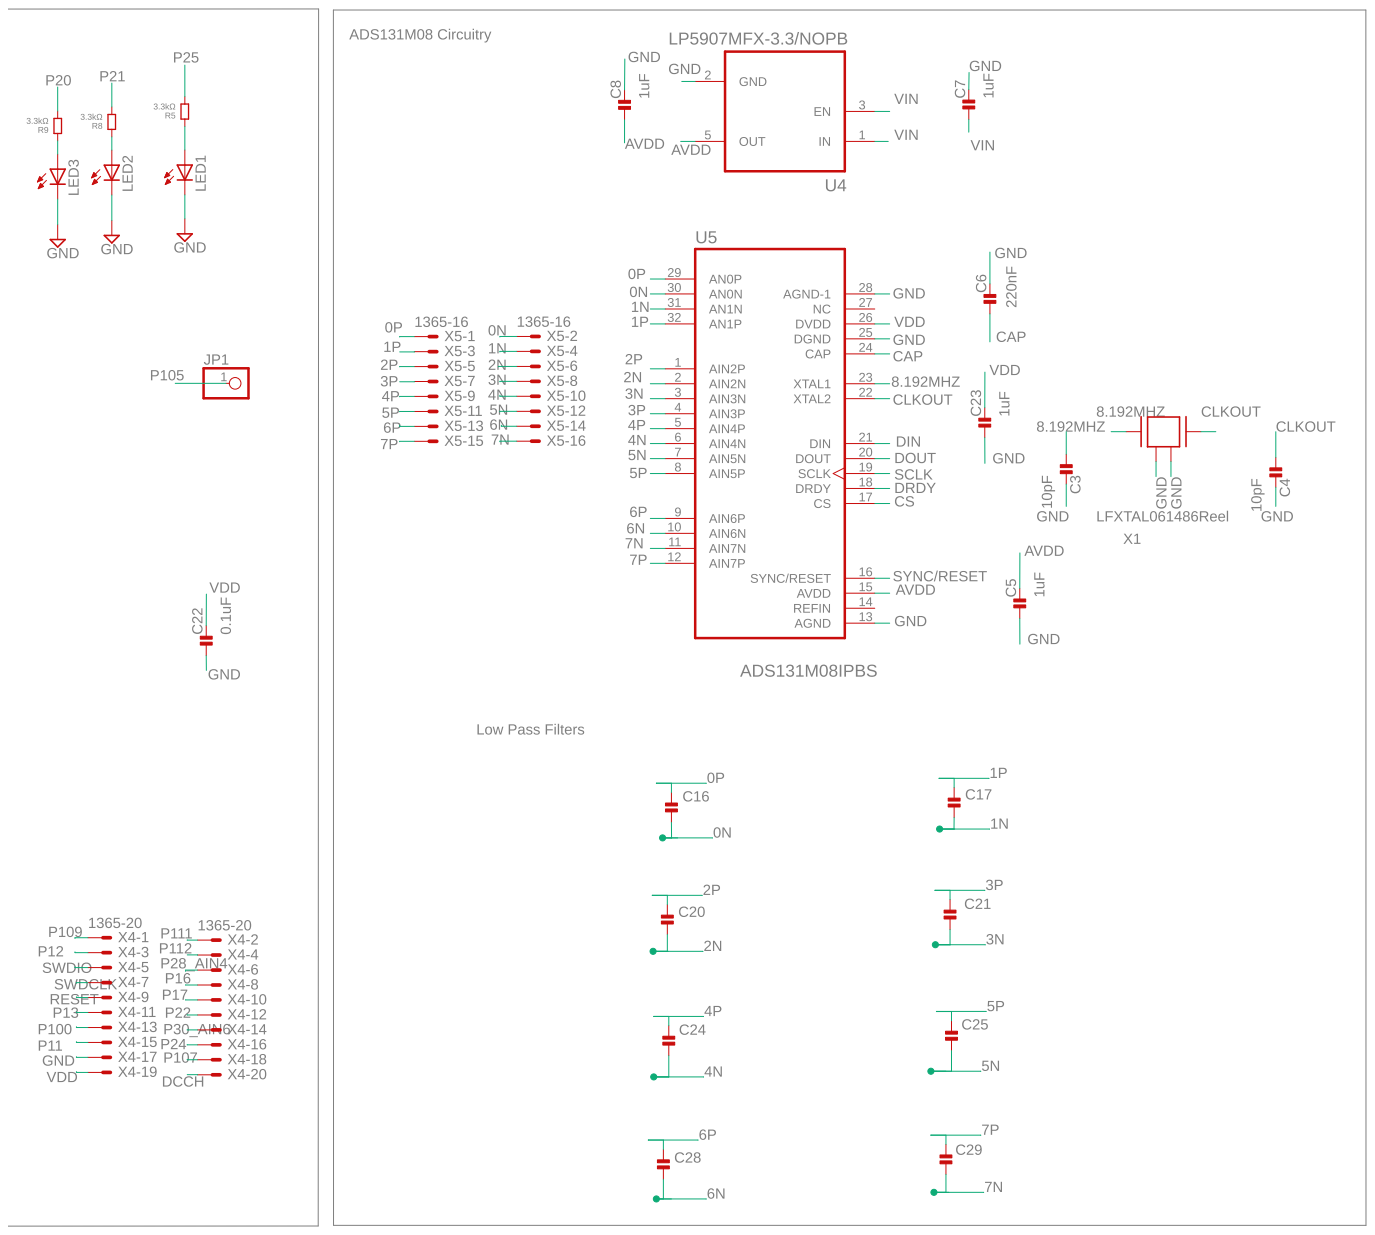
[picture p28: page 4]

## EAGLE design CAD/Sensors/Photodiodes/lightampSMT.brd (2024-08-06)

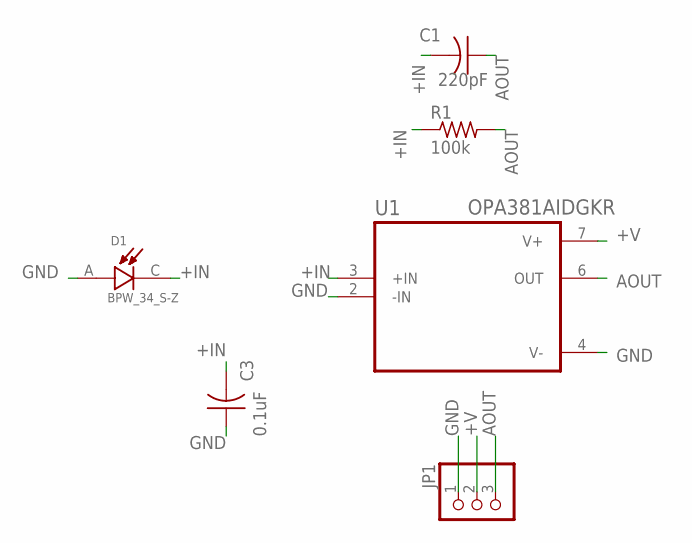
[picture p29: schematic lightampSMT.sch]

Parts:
C1: 220pF; C0603K
C3: 0.1uF; C0603K
D1: BPW_34_S-Z; DIO_BPW_34_S-Z
JP1: PINHD-1X3; 1X03
R1: 100k; R0603
U1: OPA381AIDGKR; SOP65P490X110-8N

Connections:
+IN: C1.2, C3.2, D1.C, R1.1, U1.3 (+IN)
+V: JP1.2, U1.7 (V+)
AOUT: C1.1, JP1.3, R1.2, U1.6 (OUT)
GND: C3.1, D1.A, JP1.1, U1.2 (-IN), U1.4 (V-)

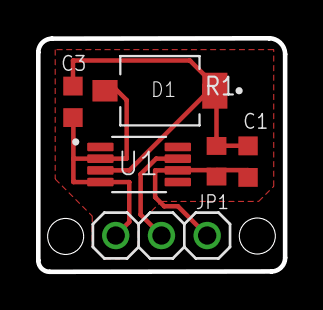
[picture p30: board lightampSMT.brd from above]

Board: 2 copper layers, 13.7 x 13.0 mm, 6 parts (0 on the bottom side), 4 nets.

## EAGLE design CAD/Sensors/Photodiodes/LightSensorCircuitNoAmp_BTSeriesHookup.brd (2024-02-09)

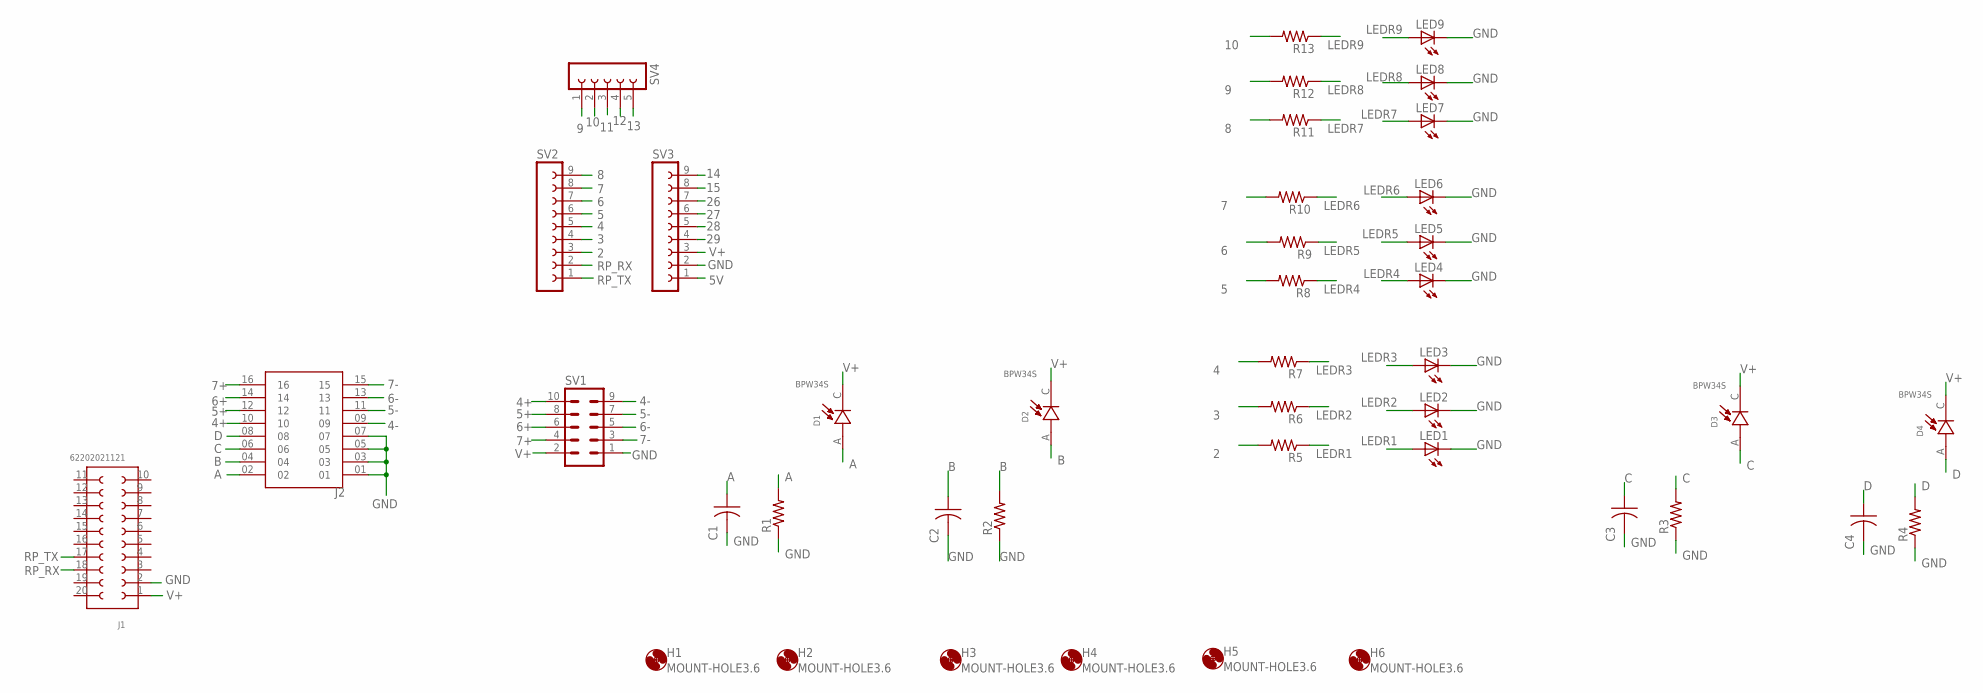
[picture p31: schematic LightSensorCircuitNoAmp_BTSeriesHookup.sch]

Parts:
C1, C2, C3, C4: C-US025-025X050; C025-025X050
D1, D2, D3, D4: BPW34S; DIO_BPW34S
H1, H2, H3, H4, H5, H6: MOUNT-HOLE3.6; 3,6
J1: 62202021121
J2: FTSH-108-02-LM-D-ES; SAMTEC_FTSH-108-02-LM-D-ES
LED1, LED2, LED3, LED4, LED5, LED6, LED7, LED8, LED9: LEDCHIPLED_1206; CHIPLED_1206
R1, R2, R3, R4, R5, R6, R7, R8, R9, R10, R11, R12, R13: R-US_0204/5; 0204/5
SV1: MA05-2
SV2, SV3: FE09-1; FE09
SV4: FE05-1

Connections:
2: R5.2, SV2.3
3: R6.2, SV2.4
4: R7.2, SV2.5
4+: J2.10, SV1.10
4-: J2.09, SV1.9
5: R8.2, SV2.6
5+: J2.12, SV1.8
5-: J2.11, SV1.7
5V: SV3.1
6: R9.2, SV2.7
6+: J2.14, SV1.6
6-: J2.13, SV1.5
7: R10.2, SV2.8
7+: J2.16, SV1.4
7-: J2.15, SV1.3
8: R11.2, SV2.9
9: R12.2, SV4.1
10: R13.2, SV4.2
11: SV4.3
12: SV4.4
13: SV4.5
14: SV3.9
15: SV3.8
26: SV3.7
27: SV3.6
28: SV3.5
29: SV3.4
A: C1.1, D1.A, J2.02, R1.2
B: C2.1, D2.A, J2.04, R2.2
C: C3.1, D3.A, J2.06, R3.2
D: C4.1, D4.A, J2.08, R4.2
GND: C1.2, C2.2, C3.2, C4.2, J1.2, J2.01, J2.03, J2.05, J2.07, LED1.C, LED2.C, LED3.C, LED4.C, LED5.C, LED6.C, LED7.C, LED8.C, LED9.C, R1.1, R2.1, R3.1, R4.1, SV1.1, SV3.2
LEDR1: LED1.A, R5.1
LEDR2: LED2.A, R6.1
LEDR3: LED3.A, R7.1
LEDR4: LED4.A, R8.1
LEDR5: LED5.A, R9.1
LEDR6: LED6.A, R10.1
LEDR7: LED7.A, R11.1
LEDR8: LED8.A, R12.1
LEDR9: LED9.A, R13.1
RP_RX: J1.18, SV2.2
RP_TX: J1.17, SV2.1
V+: D1.C, D2.C, D3.C, D4.C, J1.1, SV1.2, SV3.3

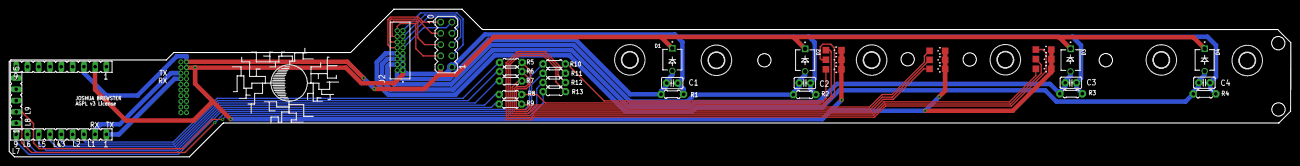
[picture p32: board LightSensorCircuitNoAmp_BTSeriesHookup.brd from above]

Board: 2 copper layers, 288.6 x 33.2 mm, 42 parts (1 on the bottom side), 34 nets.

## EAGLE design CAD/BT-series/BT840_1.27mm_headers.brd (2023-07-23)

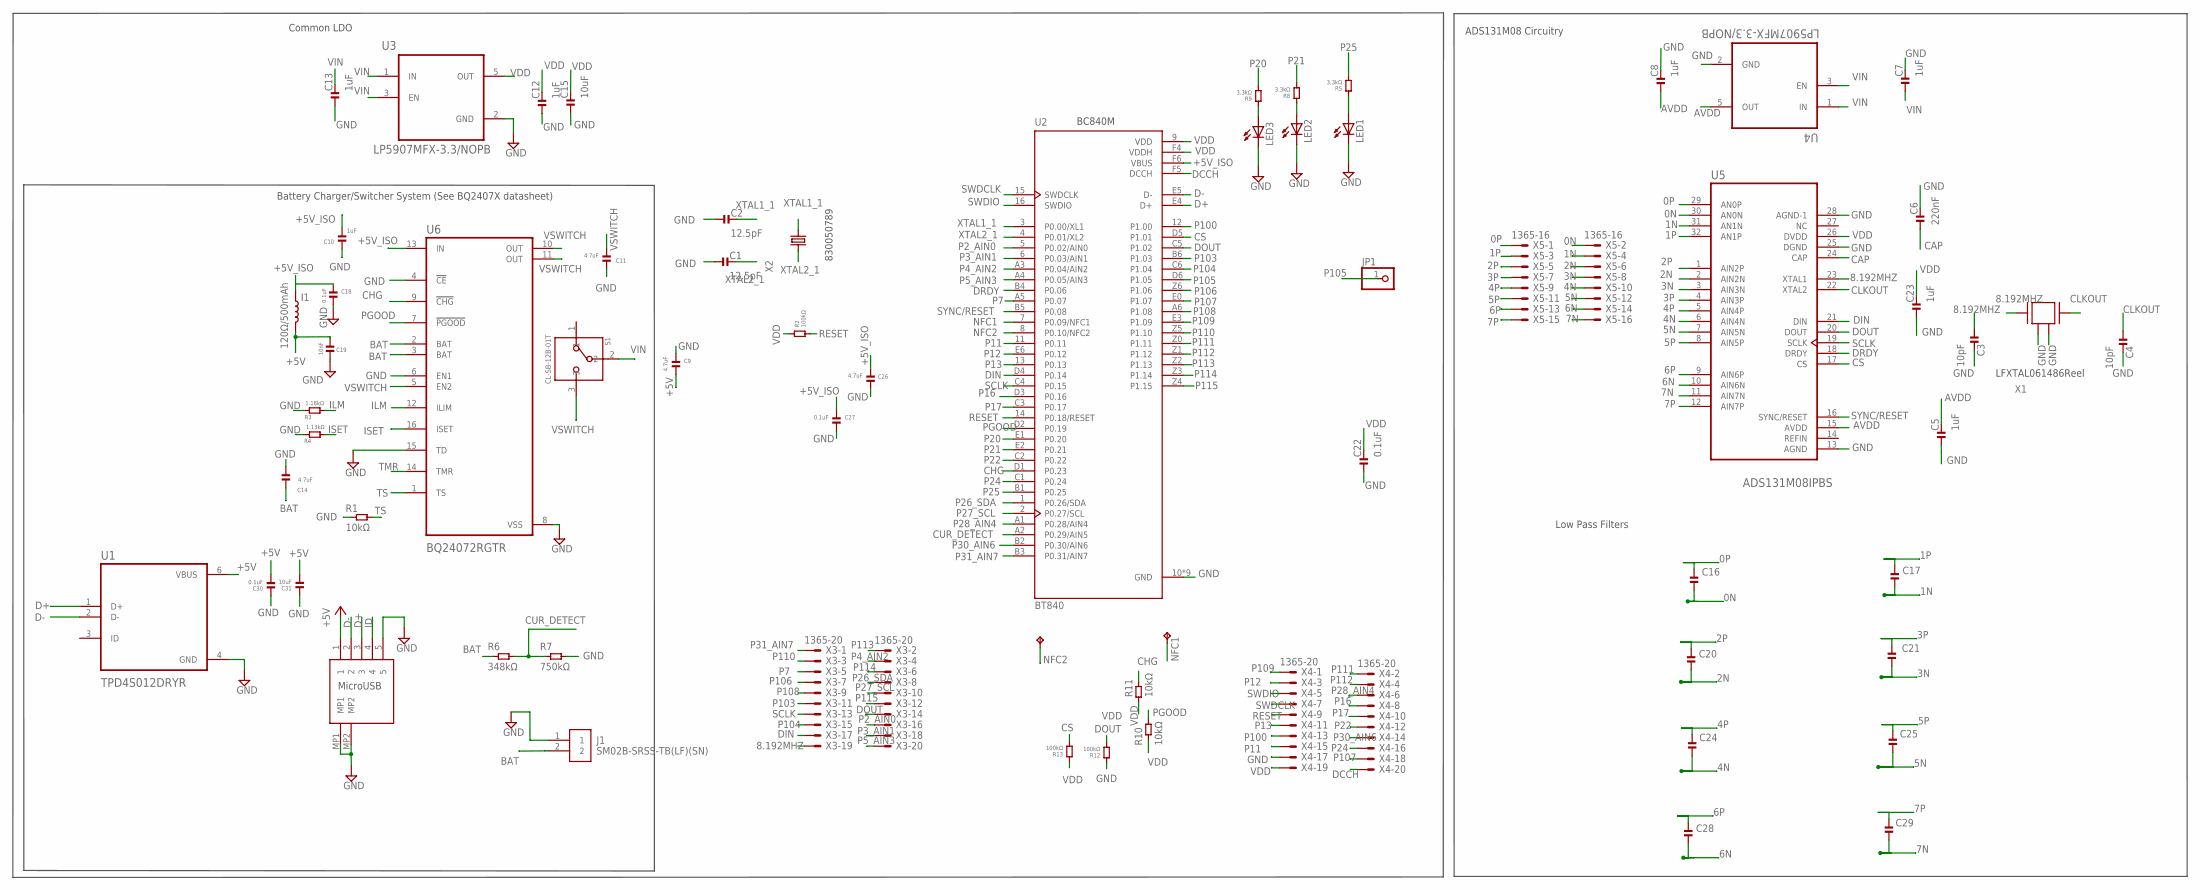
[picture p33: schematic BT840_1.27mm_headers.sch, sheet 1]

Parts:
C1, C2: 12.5pF; 0201
C3, C4: 10pF; 0201
C5, C7, C8, C10, C12, C13, C23: 1uF; 0201
C6: 220nF; 0201
C9, C11, C14, C26: 4.7uF; 0201
C15, C31: 10uF; 0402
C16, C17, C20, C21, C24, C25, C28, C29: 100pF; 0201
C18, C22, C27, C30: 0.1uF; 0201
C19: 10nF; 0201
I1: 120Ω/500mAh; 0402_COILCRAFT
J1: SM02B-SRSS-TB(LF)(SN)
JP1: PINHD-1X1; 1X01
LED1, LED2, LED3: LEDCHIPLED_0603; CHIPLED_0603
NFC1, NFC2: TPTP14SQ; TP14SQ
R1: 10kΩ; 0201
R2: 100kΩ; 0201
R3: 1.18kΩ; 0201
R4: 1.13kΩ; 0201
R5, R8, R9: 3.3kΩ; 0201
R6: 348kΩ; 0201
R7: 750kΩ; 0201
R10, R11: 10kΩ; 0402
R12, R13: 100kΩ; 0402
S1: CL-SB-12B-01T; CL-SB-12B
U1: TPD4S012DRYR; PSON50P145X100X60-6N
U2: BT840; XCVR_BT840
U3, U4: LP5907MFX-3.3/NOPB; SOT95P280X145-5N
U5: ADS131M08IPBS; QFP50P700X700X120-32N
U6: BQ24072RGTR; QFN50P300X300X100-17N
U7: DX4R005JJ2R1800
X1: ABM3B-8.000MHZ-B2-T
X2: FC-12M
X3, X4: 1365-20
X5: 1365-16

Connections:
0N: C16.2, U5.30 (AN0N), X5.2
0P: C16.1, U5.29 (AN0P), X5.1
1N: C17.2, U5.31 (AN1N), X5.4
1P: C17.1, U5.32 (AN1P), X5.3
2N: C20.2, U5.2 (AIN2N), X5.6
2P: C20.1, U5.1 (AIN2P), X5.5
3N: C21.2, U5.3 (AIN3N), X5.8
3P: C21.1, U5.4 (AIN3P), X5.7
4N: C24.2, U5.6 (AIN4N), X5.10
4P: C24.1, U5.5 (AIN4P), X5.9
5N: C25.2, U5.7 (AIN5N), X5.12
5P: C25.1, U5.8 (AIN5P), X5.11
6N: C28.2, U5.10 (AIN6N), X5.14
6P: C28.1, U5.9 (AIN6P), X5.13
7N: C29.2, U5.11 (AIN7N), X5.16
7P: C29.1, U5.12 (AIN7P), X5.15
8.192MHZ: C3.1, U5.23 (XTAL1), X1.1, X3.19
+5V: C9.2, C19.2, C30.2, C31.2, I1.P$2 (2), U1.6 (VBUS), U7.1
+5V_ISO: C10.2, C18.1, C26.2, C27.2, I1.P$1 (1), U2.F6 (VBUS), U6.13 (IN)
AVDD: C5.2, C8.1, U4.5 (OUT), U5.15 (AVDD)
BAT: C14.2, J1.2, R6.1, U6.2 (BAT), U6.3 (BAT)
CAP: C6.1, U5.24 (CAP)
CHG: R11.2, U2.D1 (P0.23), U6.9 (!CHG)
CLKOUT: C4.1, U5.22 (XTAL2), X1.3
CS: R13.1, U2.D5 (P1.01), U5.17 (CS)
CUR_DETECT: R6.2, R7.1, U2.A2 (P0.29/AIN5)
D+: U1.1 (D+), U2.E4 (D+), U7.3
D-: U1.2 (D-), U2.E5 (D-), U7.2
DCCH: U2.F5 (DCCH), X4.20
DIN: U2.D4 (P0.14), U5.21 (DIN), X3.17
DOUT: R12.1, U2.C5 (P1.02), U5.20 (DOUT), X3.14
DRDY: U2.B4 (P0.06), U5.18 (DRDY)
GND: C1.1, C2.1, C3.2, C4.2, C5.1, C6.2, C7.2, C8.2, C9.1, C10.1, C11.1, C12.1, C13.1, C14.1, C15.1, C18.2, C19.1, C22.1, C23.1, C26.1, C27.1, C30.1, C31.1, J1.1, LED1.C, LED2.C, LED3.C, R1.1, R3.1, R4.1, R7.2, R12.2, U1.4 (GND), U2.10 (GND), U2.A0 (GND), U2.B0 (GND), U2.C0 (GND), U2.D0 (GND), U2.F0 (GND), U2.F1 (GND), U2.F2 (GND), U2.F3 (GND), U3.2 (GND), U4.2 (GND), U5.13 (AGND), U5.25 (DGND), U5.28 (AGND-1), U6.4 (!CE), U6.6 (EN1), U6.8 (VSS), U6.15 (TD), U7.5, U7.MP1, U7.MP2, X1.2, X1.4, X4.17
ID: U7.4
ILM: R3.2, U6.12 (ILIM)
ISET: R4.2, U6.16 (ISET)
LED1: LED1.A, R5.2
LED2: LED2.A, R8.2
LED3: LED3.A, R9.2
NFC1: NFC2.TP, U2.7 (P0.09/NFC1)
NFC2: NFC1.TP, U2.8 (P0.10/NFC2)
P2_AIN0: U2.5 (P0.02/AIN0), X3.16
P3_AIN1: U2.6 (P0.03/AIN1), X3.18
P4_AIN2: U2.A3 (P0.04/AIN2), X3.4
P5_AIN3: U2.A4 (P0.05/AIN3), X3.20
P7: U2.A5 (P0.07), X3.5
P11: U2.11 (P0.11), X4.15
P12: U2.E6 (P0.12), X4.3
P13: U2.13 (P0.13), X4.11
P16: U2.D3 (P0.16), X4.8
P17: U2.C3 (P0.17), X4.10
P20: R9.1, U2.E1 (P0.20)
P21: R8.1, U2.E2 (P0.21)
P22: U2.C2 (P0.22), X4.12
P24: U2.C1 (P0.24), X4.16
P25: R5.1, U2.B1 (P0.25)
P26_SDA: U2.1 (P0.26/SDA), X3.8
P27_SCL: U2.2 (P0.27/SCL), X3.10
P28_AIN4: U2.A1 (P0.28/AIN4), X4.6
P30_AIN6: U2.B2 (P0.30/AIN6), X4.14
P31_AIN7: U2.B3 (P0.31/AIN7), X3.1
P100: U2.12 (P1.00), X4.13
P103: U2.B6 (P1.03), X3.11
P104: U2.C6 (P1.04), X3.15
P105: JP1.1, U2.D6 (P1.05)
P106: U2.Z6 (P1.06), X3.7
P107: U2.E0 (P1.07), X4.18
P108: U2.A6 (P1.08), X3.9
P109: U2.E3 (P1.09), X4.1
P110: U2.Z5 (P1.10), X3.3
P111: U2.Z0 (P1.11), X4.2
P112: U2.Z1 (P1.12), X4.4
P113: U2.Z2 (P1.13), X3.2
P114: U2.Z3 (P1.14), X3.6
P115: U2.Z4 (P1.15), X3.12
PGOOD: R10.2, U2.D2 (P0.19), U6.7 (!PGOOD)
RESET: R2.1, U2.14 (P0.18/RESET), X4.9
SCLK: U2.C4 (P0.15), U5.19 (SCLK), X3.13
SWDCLK: U2.15 (SWDCLK), X4.7
SWDIO: U2.16 (SWDIO), X4.5
SYNC/RESET: U2.B5 (P0.08), U5.16 (SYNC/RESET)
TMR: U6.14 (TMR)
TS: R1.2, U6.1 (TS)
VDD: C12.2, C15.2, C22.2, C23.2, R2.2, R10.1, R11.1, R13.2, U2.9 (VDD), U2.F4 (VDDH), U3.5 (OUT), U5.26 (DVDD), X4.19
VIN: C7.1, C13.2, S1.2, U3.1 (IN), U3.3 (EN), U4.1 (IN), U4.3 (EN)
VSWITCH: C11.2, S1.3, U6.5 (EN2), U6.10 (OUT), U6.11 (OUT)
XTAL1_1: C2.2, U2.3 (P0.00/XL1), X2.2
XTAL2_1: C1.2, U2.4 (P0.01/XL2), X2.1

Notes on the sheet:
LFXTAL061486Reel
830050789
MicroUSB
Battery Charger/Switcher System (See BQ2407X datasheet)
ADS131M08 Circuitry
Common LDO
BC840M
Low Pass Filters

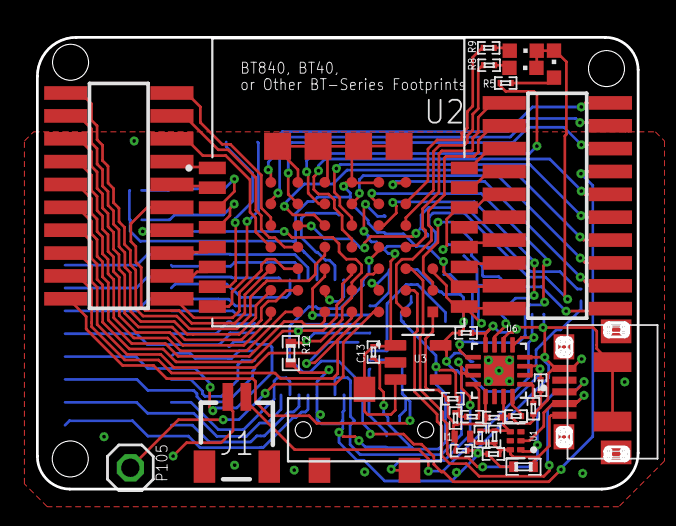
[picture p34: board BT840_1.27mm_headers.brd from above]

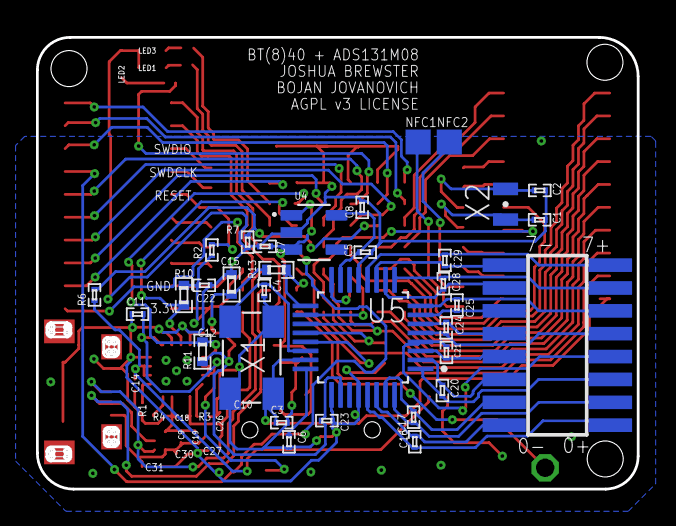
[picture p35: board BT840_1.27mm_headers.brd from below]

Board: 2 copper layers, 33.4 x 25.1 mm, 65 parts (33 on the bottom side), 86 nets.

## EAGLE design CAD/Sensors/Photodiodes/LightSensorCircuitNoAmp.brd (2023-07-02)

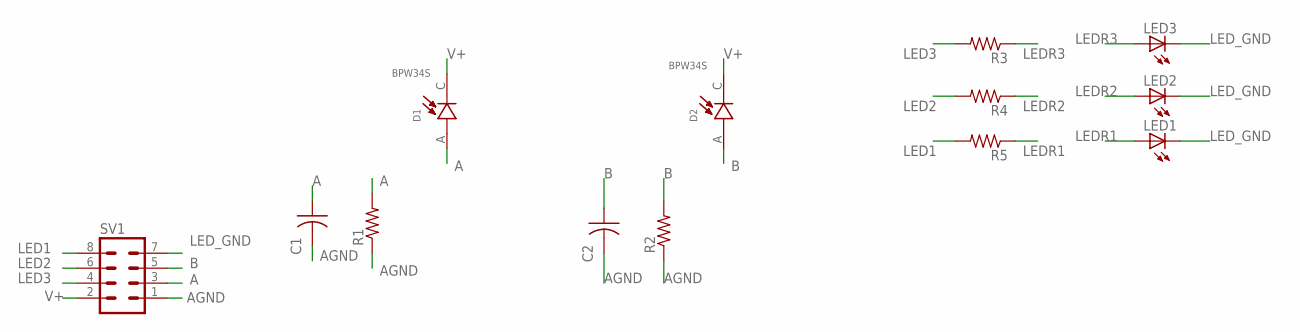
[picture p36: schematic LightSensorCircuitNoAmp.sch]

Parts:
C1, C2: C-US025-025X050; C025-025X050
D1, D2: BPW34S; DIO_BPW34S
LED1, LED2, LED3: LEDCHIPLED_1206; CHIPLED_1206
R1, R2, R3, R4, R5: R-US_0204/5; 0204/5
SV1: MA04-2

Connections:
A: C1.1, D1.A, R1.2, SV1.3
AGND: C1.2, C2.2, R1.1, R2.1, SV1.1
B: C2.1, D2.A, R2.2, SV1.5
LED1: R5.2, SV1.8
LED2: R4.2, SV1.6
LED3: R3.2, SV1.4
LEDR1: LED1.A, R5.1
LEDR2: LED2.A, R4.1
LEDR3: LED3.A, R3.1
LED_GND: LED1.C, LED2.C, LED3.C, SV1.7
V+: D1.C, D2.C, SV1.2

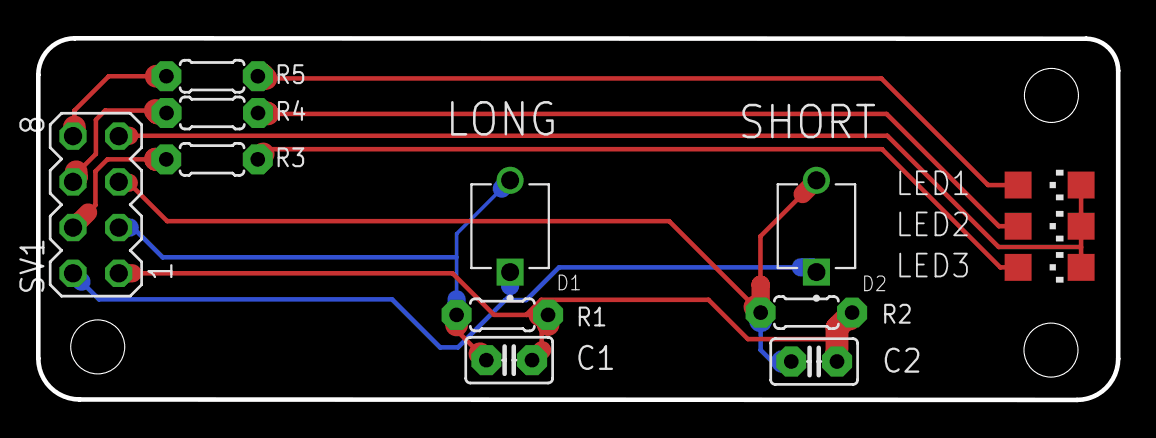
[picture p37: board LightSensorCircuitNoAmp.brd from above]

Board: 2 copper layers, 60.0 x 20.1 mm, 13 parts (0 on the bottom side), 11 nets.

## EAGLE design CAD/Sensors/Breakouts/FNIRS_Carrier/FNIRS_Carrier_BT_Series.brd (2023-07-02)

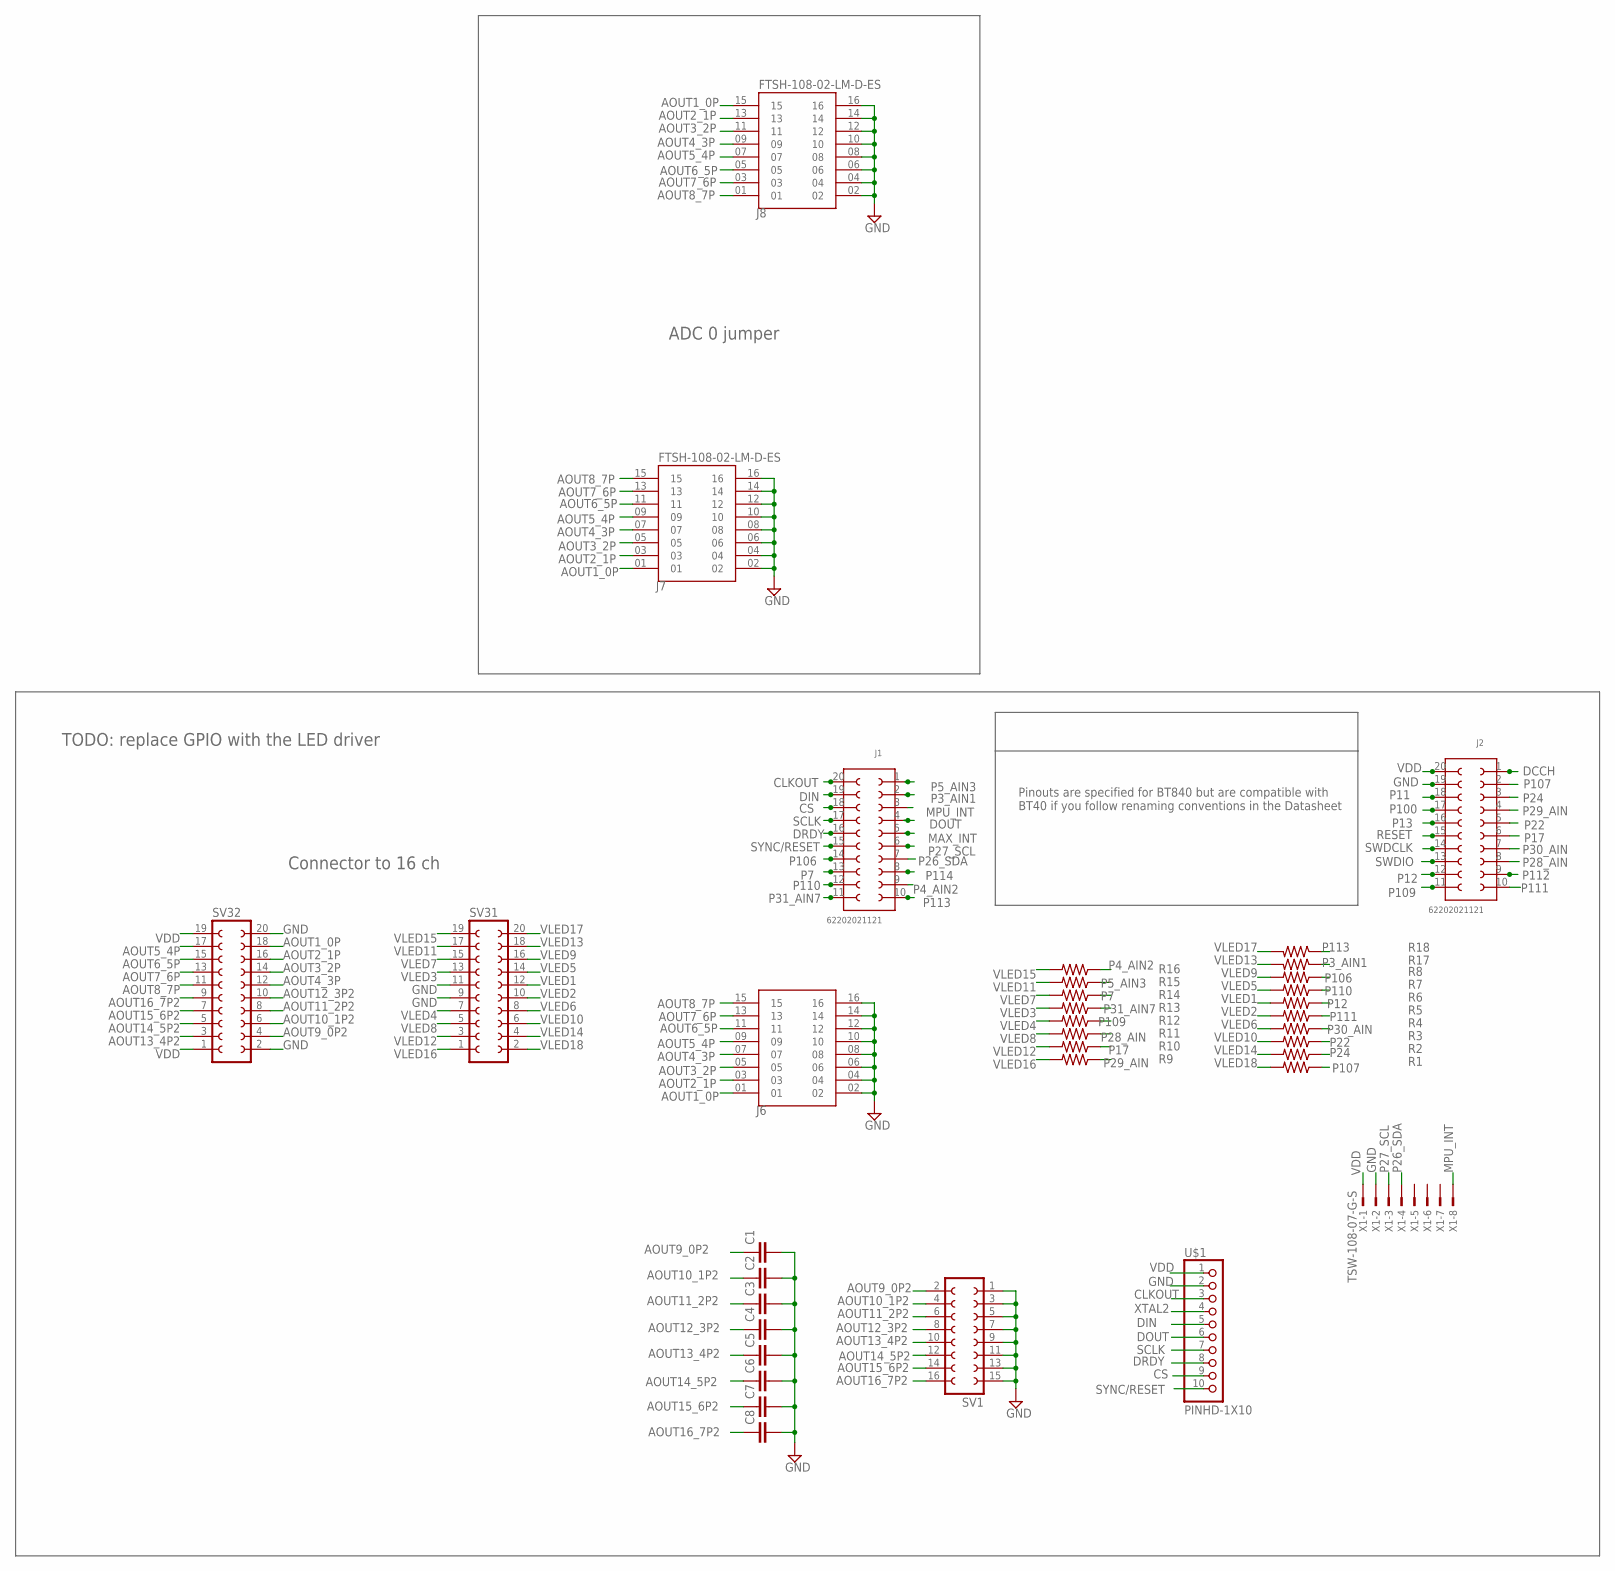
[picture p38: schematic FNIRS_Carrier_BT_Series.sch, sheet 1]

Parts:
C1, C2, C3, C4, C5, C6, C7, C8: C2.5/2; C2.5-2
J1, J2: 62202021121
J6, J7, J8: FTSH-108-02-LM-D-ES; SAMTEC_FTSH-108-02-LM-D-ES
R1, R2, R3, R4, R5, R6, R7, R8, R9, R10, R11, R12, R13, R14, R15, R16, R17, R18: R-US_0204/5; 0204/5
SV1: FE08-2
SV31, SV32: FE10-2
U$1: PINHD-1X10; 1X10-BIG
X1: TSW-108-07-G-S; TSW-108-XX-G-S

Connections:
AOUT1_0P: J6.01, J7.01, J8.15, SV32.18
AOUT2_1P: J6.03, J7.03, J8.13, SV32.16
AOUT3_2P: J6.05, J7.05, J8.11, SV32.14
AOUT4_3P: J6.07, J7.07, J8.09, SV32.12
AOUT5_4P: J6.09, J7.09, J8.07, SV32.17
AOUT6_5P: J6.11, J7.11, J8.05, SV32.15
AOUT7_6P: J6.13, J7.13, J8.03, SV32.13
AOUT8_7P: J6.15, J7.15, J8.01, SV32.11
AOUT9_0P2: C1.1, SV1.2, SV32.4
AOUT10_1P2: C2.1, SV1.4, SV32.6
AOUT11_2P2: C3.1, SV1.6, SV32.8
AOUT12_3P2: C4.1, SV1.8, SV32.10
AOUT13_4P2: C5.1, SV1.10, SV32.3
AOUT14_5P2: C6.1, SV1.12, SV32.5
AOUT15_6P2: C7.1, SV1.14, SV32.7
AOUT16_7P2: C8.1, SV1.16, SV32.9
CLKOUT: J1.20, U$1.3
CS: J1.18, U$1.9
DCCH: J2.1
DIN: J1.19, U$1.5
DOUT: J1.4, U$1.6
DRDY: J1.16, U$1.8
GND: C1.2, C2.2, C3.2, C4.2, C5.2, C6.2, C7.2, C8.2, J2.19, J6.02, J6.04, J6.06, J6.08, J6.10, J6.12, J6.14, J6.16, J7.02, J7.04, J7.06, J7.08, J7.10, J7.12, J7.14, J7.16, J8.02, J8.04, J8.06, J8.08, J8.10, J8.12, J8.14, J8.16, SV1.1, SV1.3, SV1.5, SV1.7, SV1.9, SV1.11, SV1.13, SV1.15, SV31.9, SV31.11, SV32.2, SV32.20, U$1.2, X1.2
MAX_INT: J1.5
MPU_INT: J1.3, X1.8
P3_AIN1: J1.2, R17.1
P4_AIN2: J1.9, R16.1
P5_AIN3: J1.1, R15.1
P7: J1.13, R14.1
P11: J2.18
P12: J2.12, R6.1
P13: J2.16
P17: J2.6, R10.1
P22: J2.5, R3.1
P24: J2.3, R2.1
P26_SDA: J1.7, X1.4
P27_SCL: J1.6, X1.3
P28_AIN: J2.8, R11.1
P29_AIN: J2.4, R9.1
P30_AIN: J2.7, R4.1
P31_AIN7: J1.11, R13.1
P100: J2.17
P106: J1.14, R8.1
P107: J2.2, R1.1
P109: J2.11, R12.1
P110: J1.12, R7.1
P111: J2.10, R5.1
P112: J2.9
P113: J1.10, R18.1
P114: J1.8
RESET: J2.15
SCLK: J1.17, U$1.7
SWDCLK: J2.14
SWDIO: J2.13
SYNC/RESET: J1.15, U$1.10
VDD: J2.20, SV32.1, SV32.19, U$1.1, X1.1
VLED1: R6.2, SV31.12
VLED2: R5.2, SV31.10
VLED3: R13.2, SV31.13
VLED4: R12.2, SV31.7
VLED5: R7.2, SV31.14
VLED6: R4.2, SV31.8
VLED7: R14.2, SV31.15
VLED8: R11.2, SV31.5
VLED9: R8.2, SV31.16
VLED10: R3.2, SV31.6
VLED11: R15.2, SV31.17
VLED12: R10.2, SV31.3
VLED13: R17.2, SV31.18
VLED14: R2.2, SV31.4
VLED15: R16.2, SV31.19
VLED16: R9.2, SV31.1
VLED17: R18.2, SV31.20
VLED18: R1.2, SV31.2
XTAL2: U$1.4

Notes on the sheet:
Pinouts are specified for BT840 but are compatible with BT40 if you follow renaming conventions in the Datasheet
ADC 0 jumper
Connector to 16 ch
TODO: replace GPIO with the LED driver

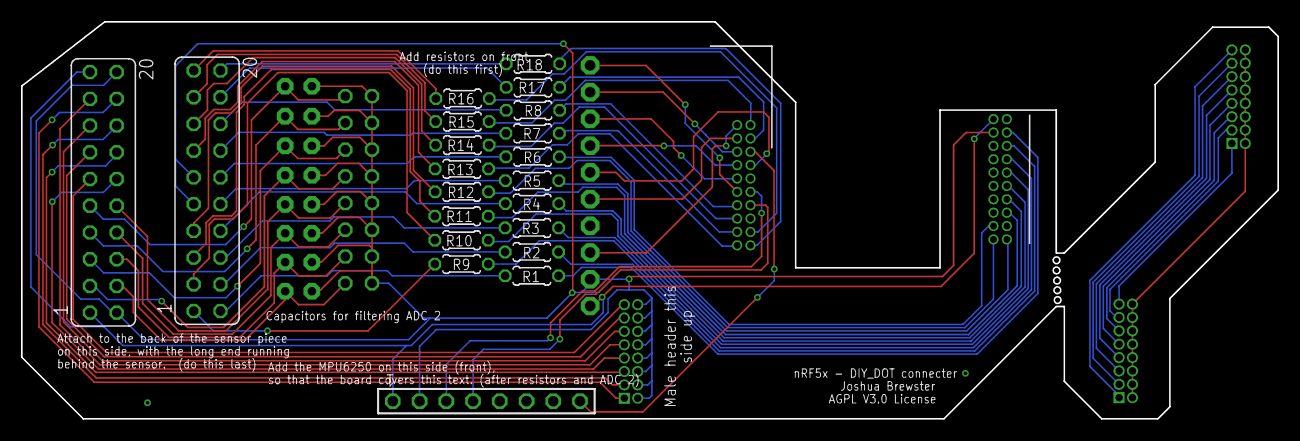
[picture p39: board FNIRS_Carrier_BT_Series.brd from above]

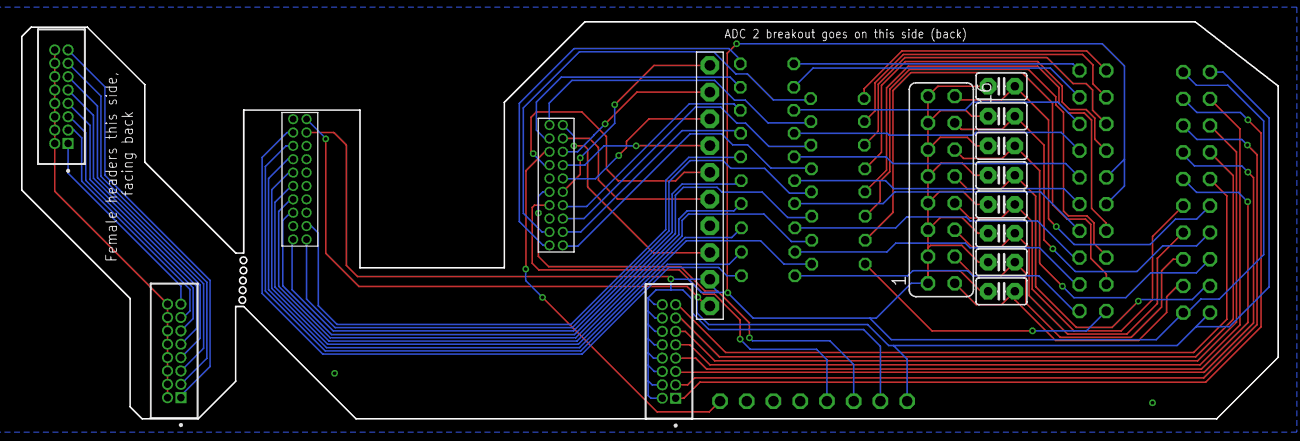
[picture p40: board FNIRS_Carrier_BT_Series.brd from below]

Board: 2 copper layers, 119.4 x 37.7 mm, 36 parts (15 on the bottom side), 64 nets.

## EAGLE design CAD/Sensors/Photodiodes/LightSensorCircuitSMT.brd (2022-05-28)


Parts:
C1, C2: 500pF; C0603
C3, C4: 0.1uF; C0603
D1, D2: BPW_34_S-Z; DIO_BPW_34_S-Z
J1: CONN_05X2NO_SILK; 2X5_NOSILK
LED1, LED2, LED3: LEDCHIPLED_1206; CHIPLED_1206
R1, R2: 100k; R0603
R3, R4, R5: R-US_R0603; R0603
U1: OPA1S2385IDRCR; DRC10_1P65X2P40_TEX

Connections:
+INA: C1.2, C3.2, D1.C, R1.1, U1.4 (+INA)
+INB: C2.2, C4.2, D2.C, R2.1, U1.6 (+INB)
AGND: C3.1, C4.1, D1.A, D2.A, J1.3, U1.3 (-INA), U1.5 (V-), U1.7 (-INB), U1.11 (EPAD)
INS: J1.2, U1.2 (INS)
LED1: J1.10, R5.2
LED2: J1.8, R4.2
LED3: J1.6, R3.2
LEDR1: LED1.A, R5.1
LEDR2: LED2.A, R4.1
LEDR3: LED3.A, R3.1
LED_GND: J1.9, LED1.C, LED2.C, LED3.C
OUTA: C1.1, J1.1, R1.2, U1.1 (OUTA)
OUTB: C2.1, J1.7, R2.2, U1.8 (OUTB)
SWITCHB: J1.4, U1.10 (SC)
V+: J1.5, U1.9 (V+)


Board: 2 copper layers, 60.0 x 20.1 mm, 16 parts (0 on the bottom side), 15 nets.

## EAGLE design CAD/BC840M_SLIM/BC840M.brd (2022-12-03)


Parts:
C1, C2: 12.5pF; 0201
C3, C4: 10pF; 0201
C5, C7, C8, C10, C12, C13, C23: 1uF; 0201
C6: 220nF; 0201
C9, C11, C14, C26: 4.7uF; 0201
C15, C31: 10uF; 0402
C16, C17, C20, C21, C24, C25, C28, C29: 100pF; 0201
C18, C22, C27, C30: 0.1uF; 0201
C19: 10nF; 0201
I1: 120Ω/500mAh; 0402_COILCRAFT
J1: SM02B-SRSS-TB(LF)(SN)
LED1, LED2, LED3: LEDCHIPLED_0603; CHIPLED_0603
NFC1, NFC2: TPTP14SQ; TP14SQ
R1: 10kΩ; 0201
R2: 100kΩ; 0201
R3: 1.18kΩ; 0603
R4: 1.13kΩ; 0603
R5, R26, R27: 3.3kΩ; 0201
R22, R25: 0Ω; 0805
R23: 348kΩ; 0603
R24: 750kΩ; 0603
R28, R29: 10kΩ; 0402
R30, R31: 100kΩ; 0402
S1: CL-SB-12B-01T; CL-SB-12B
TP1: TPTP15R; TP15R
U1: TPD4S012DRYR; PSON50P145X100X60-6N
U2: BC840M
U3, U4: LP5907MFX-3.3/NOPB; SOT95P280X145-5N
U6: BQ24072RGTR; QFN50P300X300X100-17N
U7: DX4R005JJ2R1800
U8: ADS131M08IRSNRRSN0032B-MFG; RSN0032B-MFG
X1: ABM3B-8.000MHZ-B2-T
X2: FC-12M

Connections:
0N: C16.2, U8.30 (AIN0N)
0P: C16.1, U8.29 (AIN0P)
1N: C17.2, U8.31 (AIN1N)
1P: C17.1, U8.32 (AIN1P)
2N: C20.2, U8.2 (AIN2N)
2P: C20.1, U8.1 (AIN2P)
3N: C21.2, U8.3 (AIN3N)
3P: C21.1, U8.4 (AIN3P)
4N: C24.2, U8.6 (AIN4N)
4P: C24.1, U8.5 (AIN4P)
5N: C25.2
5P: C25.1
6N: C28.2, U8.10 (AIN6N)
6P: C28.1, U8.9 (AIN6P)
7N: C29.2, U8.11 (AIN7N)
7P: C29.1, U8.12 (AIN7P)
+5V: C9.2, C19.2, C30.2, C31.2, I1.P$2 (2), U1.6 (VBUS), U7.1
+5V_ISO: C10.2, C18.1, C26.2, C27.2, I1.P$1 (1), U2.B5 (B5/VBUS), U6.13 (IN)
AVDD: C5.2, C8.1, U4.5 (OUT), U8.15 (AVDD)
BAT: C14.2, J1.2, R23.1, U6.2 (BAT), U6.3 (BAT)
CAP: C6.1, U8.24 (CAP)
CHG: R29.2, U2.D6 (D6/P027), U6.9 (!CHG)
CLKIN: C3.1, U8.23 (XTAL1_CLKIN), X1.1
CLKOUT: C4.1, U8.22 (XTAL2), X1.3
CS: R31.1, U2.E3 (E3/P115), U8.17 (CS_N)
CUR_DETECT: R23.2, R24.1, U2.E7 (E7/P004)
D+: U1.1 (D+), U2.A4 (A4/D+), U7.3
D-: U1.2 (D-), U2.A5 (A5/D-), U7.2
DCCH: U2.A6 (A6/DCCH)
DIN: U2.E0 (E0/P103), U8.21 (DIN)
DOUT: R30.1, U2.F2 (F2/P102), U8.20 (DOUT)
DRDY: U2.D1 (D1/P105), U8.18 (DRDY_N)
GND: C1.1, C2.1, C3.2, C4.2, C5.1, C6.2, C7.2, C8.2, C9.1, C10.1, C11.1, C12.1, C13.1, C14.1, C15.1, C18.2, C19.1, C22.1, C23.1, C26.1, C27.1, C30.1, C31.1, J1.1, LED1.C, LED2.C, LED3.C, R1.1, R3.1, R4.1, R22.1, R22.2, R24.2, R30.2, U1.4 (GND), U2.G0 (G0/VSS), U2.G4 (G4/VSS), U2.G5 (G5/VSS), U2.G6 (G6/VSS), U2.H4 (H4/VSS), U2.H5 (H5/VSS), U2.H6 (H6/VSS), U2.H7 (H7/VSS), U3.2 (GND), U4.2 (GND), U6.4 (!CE), U6.6 (EN1), U6.8 (VSS), U6.15 (TD), U7.5, U7.MP1, U7.MP2, U8.13 (AGND_2), U8.25 (DGND), U8.28 (AGND), U8.33 (EP), X1.2, X1.4
ID: U7.4
ILM: R3.2, U6.12 (ILIM)
ISET: R4.2, U6.16 (ISET)
LED1: LED1.A, R5.2
LED2: LED2.A, R26.2
LED3: LED3.A, R27.2
NFC1: NFC2.TP, U2.D2 (D2/P009)
NFC2: NFC1.TP, U2.E2 (E2/P010)
P2: U2.F4 (F4/P002)
P3: U2.H0 (H0/P003)
P5: U2.G7 (G7/P005)
P7: U2.B6 (B6/P007)
P8: U2.C7 (C7/P008)
P11: U2.D5 (D5/P011)
P12: U2.B7 (B7/P012)
P14: U2.C4 (C4/P014)
P15: U2.B3 (B3/P015)
P16: R26.1, U2.D3 (D3/P016)
P17: U2.A3 (A3/P017)
P19: U2.A2 (A2/P019)
P20: R27.1, U2.C2 (C2/P020)
P21: U2.C3 (C3/P021)
P22: U2.B2 (B2/P022)
P23: U2.F0 (F0/P023)
P24: U2.F1 (F1/P024)
P25: U2.A1 (A1/P025)
P26: R5.1, U2.E6 (E6/P026)
P28: U2.H1 (H1/P028)
P29: U2.E4 (E4/P029)
P30: U2.G1 (G1/P030)
P31: U2.E5 (E5/P031)
P101: U2.A0 (A0/P101)
P104: U2.B0 (B0/P104)
P106: U2.E1 (E1/P106)
P107: U2.C0 (C0/P107)
P108: U2.C5 (C5/P108)
P109: U2.C6 (C6/P109)
P110: U2.H2 (H2/P110)
P111: U2.G2 (G2/P111)
P113: U2.G3 (G3/P113)
P114: U2.H3 (H3/P114)
PGOOD: R28.2, U2.D7 (D7/P006), U6.7 (!PGOOD)
RESET: R2.1, U2.B4 (B4/P018/RESET)
SCLK: U2.F3 (F3/P112), U8.19 (SCLK)
SWDCLK: U2.C1 (C1/SWDCLK)
SWDIO: U2.B1 (B1/SWDIO)
SWO: U2.D0 (D0/P100)
SYNC/RESET: U2.D4 (D4/P013), U8.16 (SYNC_RESET_N)
TMR: U6.14 (TMR)
TS: R1.2, U6.1 (TS)
VDD: C12.2, C15.2, C22.2, C23.2, R25.2, R31.2, U2.F5 (F5/VDD), U3.5 (OUT), U8.26 (DVDD)
VDDH: R2.2, R25.1, R28.1, R29.1, U2.A7 (A7/VDDH)
VIN: C7.1, C13.2, S1.2, U3.1 (IN), U3.3 (EN), U4.1 (IN), U4.3 (EN)
VSWITCH: C11.2, S1.3, U6.5 (EN2), U6.10 (OUT), U6.11 (OUT)
XTAL1_1: C2.2, U2.F6 (F6/P000), X2.2
XTAL2_1: C1.2, U2.F7 (F7/P001), X2.1

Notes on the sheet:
LFXTAL061486Reel
830050789
MicroUSB
Battery Charger/Switcher System (See BQ2407X datasheet)
ADS131M08 Circuitry
Common LDO
BC840M
Low Pass Filters


Board: 2 copper layers, 60.0 x 9.1 mm, 64 parts (1 on the bottom side), 51 nets.

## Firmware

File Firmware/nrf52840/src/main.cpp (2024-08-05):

#include <zephyr.h>
#include <device.h>
#include <devicetree.h>
#include <drivers/spi.h>
#include <drivers/gpio.h>
#include <logging/log.h>
#include <sys/printk.h>

#include "ADS131M08_zephyr.hpp"
#include "max30102.hpp"
#include "mpu6050.hpp"
#include "bme280.hpp"
#include "qmc5883l.hpp"
#include "serial_controller.hpp"
#include "usb_comm_handler.hpp"
// #include "audio_module.hpp"
// #include "dmic_module.hpp"

#include "ble_service.hpp"
// Needed for OTA
#include "os_mgmt/os_mgmt.h"
#include "img_mgmt/img_mgmt.h"

// PWM // because we forgot the CLKOUT pin on a draft BT840/BT40 PCB
#include <drivers/pwm.h>


#define ADS_CS              ((uint8_t)33)  //   47 (BC840M),   33 (BT840)
#define DATA_READY_GPIO     ((uint8_t)6)  //   37 (BC840M),    6 (BT840)
#define ADS_RESET           ((uint8_t)8)  //   45 (BC840M),    8 (BT840)

#define ADS_1_CS            ((uint8_t)36)  //  42 (BC840M),    36 (BT840)
#define DATA_READY_1_GPIO   ((uint8_t)40)  //  24 (BC840M),    40 (BT840)
#define ADS_1_RESET         ((uint8_t)29)  //  29 (BC840M),    35 (BT840)

#define DBG_LED             ((uint8_t)25)  //  16 (BC840M),    25 (BT840)     
#define MAX_INT             ((uint8_t)7)  //  28 (BC840M),     7 (BT840)
#define MPU_INT             ((uint8_t)38)   //  2 (BC840M),     38 (BT840)

#define QMC5883L_DRDY       ((uint8_t)7)  //                  28 (BT840)

#define PWM_CLK         ((uint32_t)8192000) //Frequency (Hz)
#define PWM_PERIOD_NSEC ((uint8_t)122) //1/Frequency in nanosec
#define PWM_PIN         ((uint8_t)37) //(BT840 draft 1 missing the CLKOUT pin in same position)

//disable on BC840M, enable on BT840
static bool usePWM = true;

static bool useADCs = true;
static bool useLEDS = true;

static const uint8_t samplesPerLED = 3;

static uint32_t LEDt_ms = 100;
static const uint8_t nLEDs = 3;


//list the GPIO in the order we want to flash. 255 is ambient
static uint8_t LED_gpio[nLEDs] = { 
    20, 21, 255//, 15, 25, 
    /*
    255,
    12, 111,
    31, 109,
    110, 30,
    7, 28,
    106, 22,
    5, 17,
    3, 24,
    4, 29,
    113, 107
    */
};

//LEDs 1.01, 1.11 etc are 32 + the number after the decimal. 1.00 is pin 32 (pretty sure)

static uint8_t LEDn = 0;
static uint8_t LEDSampleCtr = 0;


LOG_MODULE_REGISTER(main);

/* Static Functions */
static int  gpio_init(void);
static int  sensor_gpio_int(void);
static int  setADS131_int(void);

static void interrupt_workQueue_handler(struct k_work* wrk);
static void ads131m08_1_interrupt_workQueue_handler(struct k_work* wrk);
static void max30102_interrupt_workQueue_handler(struct k_work* wrk);
static void mpu6050_interrupt_workQueue_handler(struct k_work* wrk);
static void qmc5883l_interrupt_workQueue_handler(struct k_work* wrk);

static void ads131m08_drdy_cb(const struct device *port, struct gpio_callback *cb, gpio_port_pins_t pins);
static void ads131m08_1_drdy_cb(const struct device *port, struct gpio_callback *cb, gpio_port_pins_t pins);
static void max30102_irq_cb(const struct device *port, struct gpio_callback *cb, gpio_port_pins_t pins);
static void mpu6050_irq_cb(const struct device *port, struct gpio_callback *cb, gpio_port_pins_t pins);
static void qmc5883l_irq_cb(const struct device *port, struct gpio_callback *cb, gpio_port_pins_t pins);

/* Global variables */
const struct device *gpio_0_dev;
const struct device *gpio_1_dev;
struct gpio_callback callback;
struct gpio_callback ads131m08_1_callback;
struct gpio_callback max30102_callback;
struct gpio_callback mpu6050_callback;
struct gpio_callback qmc5883l_callback;
struct k_work        interrupt_work_item;    ///< interrupt work item
struct k_work        ads131m08_1_interrupt_work_item;    ///< interrupt work item
struct k_work        max30102_interrupt_work_item;    ///< interrupt work item
struct k_work        mpu6050_interrupt_work_item;    ///< interrupt work item
struct k_work qmc5883l_interrupt_work_item;    ///< interrupt work item

static uint8_t sampleNum = 0;
static uint8_t ads131m08_1_sampleNum = 0;

static uint8_t i = 0;
static uint8_t j = 0;

static uint8_t ble_tx_buff[247] = {0};
static uint8_t ads131m08_1_ble_tx_buff[247] = {0};

// /* size of stack area used by each thread */
#define SSIZE 1024

// /* scheduling priority used by each thread */
#define TPRIORITY 7





//static uint8_t adcRawData[27] = {0};
static max30102_config max30102_default_config = {
    0x80, // Interrupt Config 1. Enable FIFO_A_FULL interrupt
    MAX30102_INTR_2_DIE_TEMP_RDY_EN, // Interrupt Config 2. Enable temperature ready interrupt
    0b01110000, // FIFO Config. Average 16 samples, FIFO Rollover Enabled, FFIO_A_FULL = 32
    0x87, // Mode config. Keep Max30102 shutdown. Multi LED mode .
    0b01110011, // Sp02 config. 800sps rate, 2048 full scale, 18-bit ADC resolution.
    {50, 50}, // LED1/LED2 config. 25.4mA typical LED current
    {0x11, 0x22}  // SLOT config. SLOT1/2 for LED1, SLOT3/4 for LED2.
};

static mpu6050_config mpu6050_default_config = {
    .sample_rate_config = 0x09,     // Sample rate = 100Hz
    .config_reg = 0x01,             // FSYNC disabled. Digital Low Pass filter enabled. 
    .gyro_config = (0x01 << 3),     // 500dps Gyro Full Scale. No Self-Tests.
    .accel_config = (0x01 << 3),    // +/-4g Accel Full Scale. No Self-Tests. 
    .fifo_config = 0x00,            // FIFO disabled.
    .interrupt_pin_config = 0xC0,    // INT active low. Open drain. Keep interrupt pin active until interrupt is cleared. Clear interrupt only by reading INT_STATUS register.
    .interrupt_config = 0x01,       // Enable only Data Ready interrupts.
    .user_control = 0x00,           // Disable FIFO
    .pwr_mgmt_1 = 0x01,             // Use PLL with X axis gyroscope as Clock Source.
    .pwr_mgmt_2 = 0x00              // Don't use Accelerometer only Low Power mode. XYZ axes of Gyro and Accel enabled. 
}; 

static qmc5883l_config qmc5883l_default_config = {
    .ctrl_reg_1 = (QMC5833L_OSR_512 << 6) | (QMC5833L_FS_8G << 4) | (QMC5833L_ODR_100Hz << 2) | (QMC5833L_MODE_STANDBY),
    .ctrl_reg_2 = 0
}; 

ADS131M08 adc;
ADS131M08 adc_1;
SerialController serial;
UsbCommHandler usbCommHandler(serial);
Max30102 max30102(usbCommHandler);
Mpu6050 mpu6050(usbCommHandler);
Bme280 bme280(usbCommHandler);
Qmc5883l qmc5883l(usbCommHandler);
//AudioModule audio;
//DmicModule dmic;



void initPWM(void) {

    const struct device *pwm;

	pwm = device_get_binding("PWM_0");

    pwm_pin_set_nsec(
        pwm, 
        PWM_PIN, 
        PWM_PERIOD_NSEC, 
        PWM_PERIOD_NSEC / 2U, 
        0
    );
}

// //////////////////////////////




static int configureGPIO(int pin, gpio_flags_t rule) {
    int ret = 0;
    if(pin < 32) {
        ret += gpio_pin_configure(gpio_0_dev, pin,       rule); 
    } else if (pin < 100) {
        ret += gpio_pin_configure(gpio_1_dev, pin - 32,  rule); 
    } else {
        ret += gpio_pin_configure(gpio_1_dev, pin - 100, rule); //supports e.g. 114 for 1.14
    }
    return ret;
}

static int configureInterrupt(int pin, gpio_flags_t rule) {
    int ret = 0;
    if(pin < 32) {
        ret += gpio_pin_interrupt_configure(gpio_0_dev, pin, rule);
    } else if (pin < 100) {
        ret += gpio_pin_interrupt_configure(gpio_1_dev, pin - 32,  rule); 
    } else {
        ret += gpio_pin_interrupt_configure(gpio_1_dev, pin - 100, rule); //supports e.g. 114 for 1.14
    }
    return ret;
}

static int addGPIOCallback(int pin, gpio_callback * gpio_cb, void (*cb)(const struct device *port, struct gpio_callback *cb, gpio_port_pins_t pins)) {
    int ret = 0;
    if(pin < 32) {
        gpio_init_callback(gpio_cb, cb, BIT(pin));    
        ret = gpio_add_callback(gpio_0_dev, gpio_cb);
    } else if (pin < 100) {
        gpio_init_callback(gpio_cb, cb, BIT(pin - 32));    
        ret = gpio_add_callback(gpio_1_dev, gpio_cb);
    } else {
        gpio_init_callback(gpio_cb, cb, BIT(pin - 100));    
        ret = gpio_add_callback(gpio_1_dev, gpio_cb); //supports e.g. 114 for 1.14
    }
    return ret;
}

static bool getGPIO(int pin) {
    bool state = false; 
    if(pin < 32) {
        if(gpio_pin_get(gpio_0_dev, pin)) {   
            state = true;
        }
    } else if (pin < 100) {
        if(gpio_pin_get(gpio_1_dev, pin-32)) {   
            state = true;
        }
    } else {
        if(gpio_pin_get(gpio_1_dev, pin-100)) {   
            state = true;
        }
    }
    return state;
} 

static int setGPIO(int pin, int state) {
    int ret = 0;
    if(pin < 32) {
        ret = gpio_pin_set(gpio_0_dev, pin, state);
    } else if (pin < 100) {
        ret = gpio_pin_set(gpio_1_dev, pin-32, state);
    } else {
        ret = gpio_pin_set(gpio_1_dev, pin-100, state);
    }
    return ret;
}

//LED routines using GPIO

static int setupLEDS() {
    int ret = 0;
    for(uint8_t i = 0; i < nLEDs; i++) {
        if(LED_gpio[i] == 255) continue;
        else if(LED_gpio[i] < 32) {
            ret += gpio_pin_configure(gpio_0_dev, LED_gpio[i], GPIO_OUTPUT_ACTIVE); 
            gpio_pin_set(gpio_0_dev, LED_gpio[i], 0);
        } else if (LED_gpio[1] < 100) {
            ret += gpio_pin_configure(gpio_1_dev, LED_gpio[i] - 32, GPIO_OUTPUT_ACTIVE); 
            gpio_pin_set(gpio_1_dev, LED_gpio[i] - 32, 0);
        } else {
            ret += gpio_pin_configure(gpio_1_dev, LED_gpio[i] - 100, GPIO_OUTPUT_ACTIVE);  //supports e.g. 114 for 1.14
            gpio_pin_set(gpio_1_dev, LED_gpio[i] - 100, 0);
        }
        
    }

    return ret;
}


static void alternateLEDs() {
    if(LED_gpio[LEDn] != 255) {
        if(LED_gpio[LEDn] < 32) {
            gpio_pin_set(gpio_0_dev, LED_gpio[LEDn], 0);
        } else if (LED_gpio[1] < 100) {
            gpio_pin_set(gpio_1_dev, LED_gpio[LEDn] - 32, 0);
        } else {
            gpio_pin_set(gpio_1_dev, LED_gpio[LEDn] - 100, 0);
        }
    }
    
    LEDn++;
    
    if (LEDn >= nLEDs) {
        LEDn = 0;
    }
    
    if(LED_gpio[LEDn] != 255) {
        if(LED_gpio[LEDn] < 32) {
            gpio_pin_set(gpio_0_dev, LED_gpio[LEDn], 1);
        } else if (LED_gpio[1] < 100) {
            gpio_pin_set(gpio_1_dev, LED_gpio[LEDn] - 32, 1);
        } else {
            gpio_pin_set(gpio_1_dev, LED_gpio[LEDn] - 100, 1);
        }
    }
}

static void incrLEDSampleCtr() {

    LEDSampleCtr++;
    if(LEDSampleCtr >= samplesPerLED) {
        //TODO: implement an LED driver chip. GPIO has bad power up time
        alternateLEDs(); //alternate to the ADC samples to time the LED pulses (for photodiode sampling)
        LEDSampleCtr = 0;
    }
}

void blink(void) {
    setupLEDS();
    while(1) {
	    alternateLEDs();
        k_msleep(LEDt_ms);
    }
}

// does not synchronize correctly
// K_THREAD_DEFINE(blink0_id, SSIZE, blink, NULL, NULL, NULL,
//         TPRIORITY, 0, 0);

static int gpio_init(void) {
    
    gpio_0_dev = device_get_binding("GPIO_0");
	if (gpio_0_dev == NULL) {
		LOG_ERR("***ERROR: GPIO_0 device binding!");
        return -1;
	}  
    gpio_1_dev = device_get_binding("GPIO_1");
	if (gpio_1_dev == NULL) {
		LOG_ERR("***ERROR: GPIO_1 device binding!");
        return -1;
	}        

    //setADS131_int();
    //ret = gpio_pin_configure(gpio_0_dev, DATA_READY_GPIO, GPIO_INPUT | GPIO_ACTIVE_LOW);
    
    configureGPIO(DBG_LED, GPIO_OUTPUT_ACTIVE); // Set SYNC/RESET pin to HIGH
    setGPIO(DBG_LED, 0);

    LOG_INF("Entering sleep...");
    k_sleep(K_MSEC(1000)); // give some time to ADS131 to settle after power on
    LOG_INF("Waking up...");

    setGPIO(DBG_LED, 1);

}

static int sensor_gpio_int(void){
	int ret = 0;


/* Max30102 Interrupt */
//TODO(bojankoce): Use Zephyr DT (device tree) macros to get GPIO device, port and pin number

    ret += configureGPIO(MAX_INT, GPIO_INPUT | GPIO_PULL_UP);
    ret += configureInterrupt(MAX_INT, GPIO_INT_EDGE_FALLING);
    ret += addGPIOCallback(MAX_INT, &max30102_callback, &max30102_irq_cb);

    if (ret != 0){
        LOG_ERR("***ERROR: GPIO initialization\n");
    } else {
        LOG_INF("Max30102 Interrupt pin Int'd!");
    }
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

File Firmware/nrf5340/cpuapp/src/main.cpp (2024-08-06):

#include <zephyr.h>
#include <device.h>
#include <devicetree.h>
#include <drivers/spi.h>
#include <drivers/gpio.h>
#include <logging/log.h>
#include <sys/printk.h>

#include "ADS131M08_zephyr.hpp"
#include "max30102.hpp"
#include "mpu6050.hpp"
#include "bme280.hpp"
#include "qmc5883l.hpp"
#include "serial_controller.hpp"
#include "usb_comm_handler.hpp"
#include "audio_module.hpp"
#include "dmic_module.hpp"

#include "ble_service.hpp"
// Needed for OTA
#include "os_mgmt/os_mgmt.h"
#include "img_mgmt/img_mgmt.h"

/* Global variables*/
const struct device *gpio_0_dev;
const struct device *gpio_1_dev;

//#include "gpio_macros.cpp"
//#include "led_testing.cpp" //pwm and LED alternating routines

//make sure the pins are updated in the .overlay file as well, and double check the prj.conf
#define ADS_CS              ((uint8_t)22)
#define DATA_READY_GPIO     ((uint8_t)15)  
#define ADS_RESET           ((uint8_t)12)  

#define ADS_1_CS            ((uint8_t)30)  // 30 //25 (nirs ensemble)
#define DATA_READY_1_GPIO   ((uint8_t)11)  // 11 //14 (nirs ensemble)
#define ADS_1_RESET         ((uint8_t)9)   // 9  //108 (nirs ensemble)

#define RED_LED             ((uint8_t)19)  //Red LED
#define GREEN_LED           ((uint8_t)37)  //GREEN LED
#define BLUE_LED            ((uint8_t)38)  //BLUE LED

#define MAX_INT             ((uint8_t)4) // 4 //113 (nirs ensemble)

#define MPU_INT             ((uint8_t)5)   // 5 //4 (nirs ensemble)
#define QMC5883L_DRDY       ((uint8_t)6)   // 6 //32 (nirs ensemble)

LOG_MODULE_REGISTER(main);

/* Static Functions */
static int  gpio_init(void);
static int  init_sensor_gpio_int(void);

#define SPS_250_OSR  0b111
#define SPS_500_OSR  0b110
#define SPS_1000_OSR 0b101
#define SPS_2000_OSR 0b100

#if CONFIG_USE_ADS131M08
/* Static Functions */
static int  init_ads131_gpio_int(void);
static void ads131m08_drdy_cb(const struct device *port, struct gpio_callback *cb, gpio_port_pins_t pins);
static void ads131m08_1_drdy_cb(const struct device *port, struct gpio_callback *cb, gpio_port_pins_t pins);
static void interrupt_workQueue_handler(struct k_work* wrk);
static void ads131m08_1_interrupt_workQueue_handler(struct k_work* wrk);
static int activate_irq_on_data_ready(void);

/* Global variables */
struct gpio_callback callback;
struct gpio_callback ads131m08_1_callback;
struct k_work interrupt_work_item;    ///< interrupt work item
struct k_work ads131m08_1_interrupt_work_item;    ///< interrupt work item

static uint8_t ble_tx_buff[247] = {0};
static uint8_t ads131m08_1_ble_tx_buff[247] = {0};
static uint8_t sampleNum = 0;
static uint8_t ads131m08_1_sampleNum = 0;
static uint8_t i = 0;
static uint8_t j = 0;
#endif 

#if CONFIG_USE_MAX30102
/* Static Functions */
static void max30102_interrupt_workQueue_handler(struct k_work* wrk);
static void max30102_irq_cb(const struct device *port, struct gpio_callback *cb, gpio_port_pins_t pins);
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

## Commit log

2021-05-31 upload new CAD files
    [BT832A.brd, BT832A.sch]
2021-06-18 finished sch
    [BT832A.brd, BT832A.sch]
2021-06-18 smaller packages
    [BT832A.brd, BT832A.sch]
2021-06-18 add switch
    [BT832A.brd, BT832A.sch]
2021-06-18 almost there
    [BT832A.brd, BT832A.sch]
2021-06-20 more edits
    [BT832A.brd, BT832A_centroid.csv, copper_bottom.gbr, copper_top.gbr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]
2021-06-24 replace with 20 pin cp2102
    [BT832 BOM.xlsx, BT832A.brd, BT832A.sch, BT832A_centroid.csv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]
2021-06-30 add both CP2102 versions
    [BT832 BOM.xlsx, BT832A.brd, BT832A.sch, BT832A_centroid.csv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]
2021-11-14 i/o prerouting
    [BC840M.brd, BC840M.sch]
2021-11-15 grounding routed
    [BC840M.brd, BC840M.sch]
2021-11-16 removed cap on ads
    [BC840M.brd, BC840M.sch]
2021-11-16 more tweaks
    [BC840M.brd, BC840M.sch]
2021-11-18 still need to add TVS diodes
    [BC840M.brd, BC840M.sch]
2021-11-18 fixed a ground
    [BC840M.brd]
2021-11-18 more layout fixes
    [BC840M.brd]
2021-11-18 more fixes
    [BC840M.brd]
2021-11-22 added TVS diodes
    [BC840M.brd, BC840M.sch]
2021-11-24 edits and CAM
    [BC840M+ADS131_BOM.xlsx, BC840M.brd, BC840M.sch, BC840M_centroid.csv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]
2021-11-24 updated BOM
    [BC840M+ADS131.xlsx, BC840M+ADS131_BOM.xlsx]
2021-11-24 fix holes for microusb
    [BC840M.brd, copper_bottom.gbr, copper_top.gbr, drill_1_16.xln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]
2021-11-28 fixed tented vias
    [BC840M+ADS131_BOM.xls, BC840M+ADS131_BOM.xlsx, BC840M.brd, copper_top.gbr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]
2022-05-28 added light sensor test circuits (plz dont buy all muh parts :3)
    [BC840M_LeftStrap.brd, BC840M_LeftStrap.sch, BC840M_RightStrap.brd, BC840M_RightStrap.sch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]
2022-06-28 Include MAX30102 module.
    Configure MAX30102 to work in preferred mode. Take the RED/IR samples from a FIFO, take the temperature reading and transfer the RED/IR samples together with the temperature over BLE using MAX30102 C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
2022-06-30 Check if MAX30102 is attached on I2C bus before start sampling.
2022-07-20 Add the second ADS131M08 sensor.
    Create separate BLE characteristics for sending samples of second ADS131M08 sensor.
2022-07-30 Add the ability to transfer sensor readings over USB serial link
2022-08-22 Take samples from BME280 sensor. Send samples over BLE and USB.
2022-08-29 Remove HEXDUMP debug print from Bme280Notify function
2022-08-30 design corrections
    [BC40M_nrf53.brd, BC40M_nrf53.sch, BC840M+ADS131_BOM.xls, BC840M.brd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]
2022-08-30 added missing voltage divider (doesn't fix the battery charger circuit)
    [BT832A.brd, BT832A.sch]
2022-09-06 Slightly change ADS131M08 initial configuration. Write 0 to RESET bit, enable DC Block Filter.
2022-10-02 added revisions and alt configurations
    [1.25mm_BC40M+ADS131_BOM.xls, 1.25mm_BC840M+ADS131_BOM.xls, 1.25mm_BT840+ADS131_BOM.xls, BC40M_nrf53.brd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]
2022-10-05 add cam outputs for bt series with some corrections
    [BT840_1.25mm_headers.brd, BT840_1.25mm_headers_centroid.csv, copper_bottom.gbr, copper_top.gbr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]
2023-01-22 reorganized repo to include each firmware revision
    [LightSensorCircuit.brd, LightSensorCircuit.sch, LightSensorCircuitSMT.brd, LightSensorCircuitSMT.sch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]
2023-03-16 fixed CLKOUT GPIO pin missing, replaced P105 breakout
    [BT840_1.25mm_headers.brd, BT840_1.25mm_headers.sch]
2023-03-16 adjusted default connection interval for nrf53 board
2023-04-13 fixed LED routine
2023-04-23 fixed nr52840 firmware for BC840M
    [BC840M_1.27mm_headers.brd, BC840M_1.27mm_headers.sch, BC840M_LeftStrap.brd, BC840M_LeftStrap.sch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]
2023-05-03 add FNIRS carrier board, testing firmware
    [FNIRS_Carrier_BT_Series.brd, FNIRS_Carrier_BT_Series.sch, copper_bottom.gbr, copper_top.gbr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]
2023-06-11 modifed io order on bt840, some nrf52840 firmware cleanup (need to update with compass and audio too)
    [BT840_1.27mm_headers.brd, BT840_1.27mm_headers.sch, FNIRS_Carrier_BT_Series.brd, FNIRS_Carrier_BT_Series.sch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]
2023-06-11 fixed cur_detect compatibility for bt40/bt840
    [BT840_1.27mm_headers.brd, BT840_1.27mm_headers.sch]
2023-06-11 broke out the last gpio
    [BT840_1.27mm_headers.brd, BT840_1.27mm_headers.sch]
2023-06-12 fixed fnirs carrier board
    [FNIRS_Carrier_BT_Series.brd, FNIRS_Carrier_BT_Series.sch, copper_bottom.gbr, copper_top.gbr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]
2023-06-16 updated cam
    [BT840+ADS131_BOM.xls, copper_bottom.gbr, copper_top.gbr, drill_1_16.xln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]
2023-06-22 minor fix
    [FNIRS_Carrier_BT_Series.brd, copper_bottom.gbr, copper_top.gbr, drill_1_16.xln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]
2023-08-21 restored overlay/main gpio config, added Beacon support
    [BT840+ADS131_BOM.xls, LightSensorCircuitNoAmp_BTSeriesHookup - Copy.brd, LightSensorCircuitNoAmp_BTSeriesHookup - Copy.sch]
2023-11-08 fixed uart3 pin
2023-11-11 Improve prj.conf
    - Remove CONFIG_USE_USB flag. It is added automatically as soon as some of the sensors that supports USB transfer is enabled (see "select USE_USB" flag in Kconfig file)
    - Fixe CONFIG_USE_BME280 flag
2023-11-11 Update Kconfig
    As soon as we select to use BME280 sensor, enable (set to =y) the following flags:
    - CONFIG_SENSOR
    - CONFIG_BME280
2023-11-11 fix, up max30102 power output
2024-01-10 pdfs for a couple boards
2024-02-07 fix pin

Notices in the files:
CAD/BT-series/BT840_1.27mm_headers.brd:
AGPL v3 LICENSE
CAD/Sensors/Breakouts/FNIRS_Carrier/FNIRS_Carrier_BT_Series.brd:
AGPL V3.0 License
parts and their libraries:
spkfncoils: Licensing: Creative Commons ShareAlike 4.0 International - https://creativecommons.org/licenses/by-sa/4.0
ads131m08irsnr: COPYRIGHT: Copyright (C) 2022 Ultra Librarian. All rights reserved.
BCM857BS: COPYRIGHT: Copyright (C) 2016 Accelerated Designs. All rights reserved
